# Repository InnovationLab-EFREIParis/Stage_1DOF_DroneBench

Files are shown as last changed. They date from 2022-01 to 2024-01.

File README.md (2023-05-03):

# Bras à un degré de liberté (1DOF Drone Bench)
Dispositif pédagogique permettant de faire découvrir quelques principes et composants que l'on peut retrouver sur un drone mais de façon largement simplifiée et en toute sécurité.  
Le principe est d'asservir un bras mobile (qui par défaut est à la verticale) à un angle voulu en pilotant le moteur et l'hélice fixés à l'extremité de ce bras. La mesure de l'angle se fait par une centrale inertielle. Le tout est controlé par un microcontrôleur relié à un PC où une interface en Python trace différentes courbes (angle en fonction des gazs, angles en fonction du temps).

# Exemple de courbe
L'interface graphique génére une page visible dans un navigateur où l'on peut voir la consigne angulaire et la position du bras évoluant au cours du temps.
Les données brut issues de la centrale sont egalement disponible, ainsi que quelques indications sur les temps de réponses, dépassement...

https://ilab.efrei.fr/html/brasdrone

# Dispositif
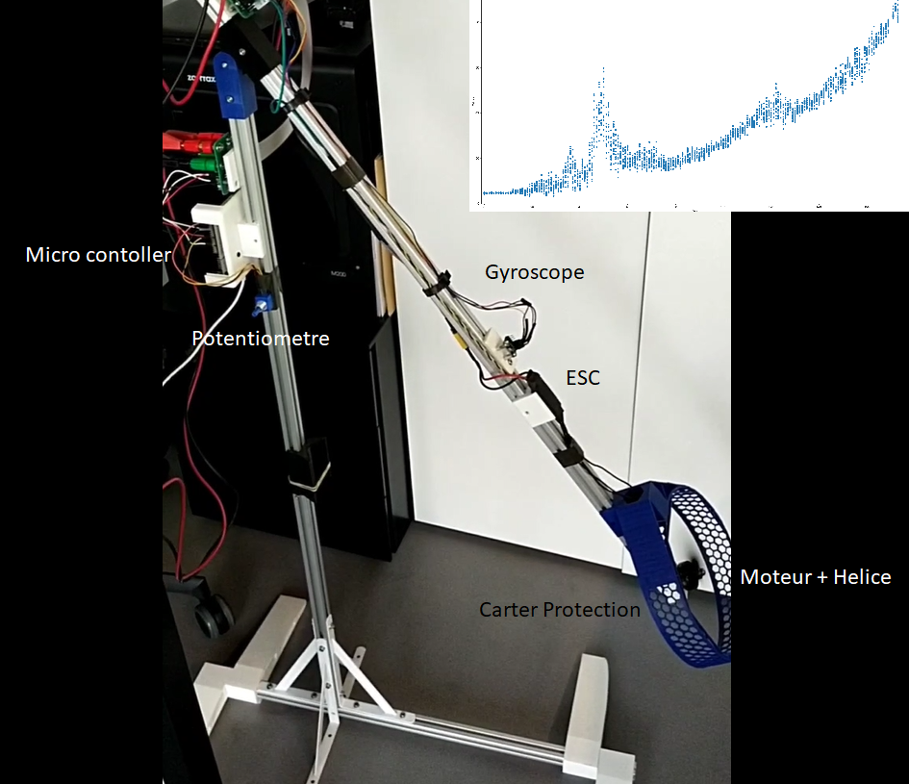
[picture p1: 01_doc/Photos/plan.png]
This is an image


[Vidéo](https://github.com/InnovationLab-EFREIParis/Stage_1DOF_DroneBench/blob/main/01_doc/Photos/video_20220902_181232.mp4)

# Utilisation
## Alimentation
La carte microcontrôleur est alimentée par USB. Il faut donc la connecter à un PC, ce qui permet egalement d'échanger des données.  
La partie moteur est alimentée par les câbles bananes. Régler l'alimentation sur 24V avec une limitation de courant à 5A.  
## Commandes
Ouvrir ensuite un [terminal série](https://github.com/InnovationLab-EFREIParis/Stage_1DOF_DroneBench/tree/main/04_UART_Term/UART_Terminal_1.2.2) puis établir la communication à 115200 bits/s.  
Le microcontrôleur se comporte comme un automate. En envoyant des commandes via la liaison série, il va entrer dans différent états, dont certains seront propres aux différents modes de fonctionnement du dispositif.  
Le mode dans lequel se trouve l'automate s'affiche à l'écran.  
Par défaut, la carte est dans l'état "Entrance" : tapez sur la touche Entrée et suivez les indications à l'écran.  
Une fois l'état "Init UC" passé, la série de "bip" émis par le moteur doit s'arrêter. Le moteur est prêt.  
L'état suivant "Motor Ready" fait office de menu de sélection de mode.  
## Mode automatique
Le mode "Auto Mode" vous permettra de renseigner une consigne de position angulaire, ainsi que des coefficients PID. Il s'agit du seul mode asservis.  
## Modes manuels
Le mode "Manual Mode Pot" vous permettra de modifier manuellement les gazs du moteur via le potentiomètre.  
Le mode "Manual Mode Term" vous permettra de jouer sur une consigne en % de gazs du moteur.  
# Conception
## Mécanique
Une bonne partie des pièces ont été conçues avec Solidworks et fabriquées en impression 3D par dépot de filament.  
Les modèles 3D sont accessibles [ici](https://github.com/InnovationLab-EFREIParis/Stage_1DOF_DroneBench/tree/main/03_mdl)  
Les montants sont en profilé d'aluminium de 20 mm dont voici la [référence](https://github.com/InnovationLab-EFREIParis/Stage_1DOF_DroneBench/tree/main/01_doc/Structure%20et%20assemblage)  
## Électronique
- [Carte microcontrôleur STM32 L476RG](https://github.com/InnovationLab-EFREIParis/Stage_1DOF_DroneBench/tree/main/01_doc/STM32)
- [Moteur et ESC](https://github.com/InnovationLab-EFREIParis/Stage_1DOF_DroneBench/tree/main/01_doc/Moteur%20et%20ESC)
- [Centrale inertielle](https://github.com/InnovationLab-EFREIParis/Stage_1DOF_DroneBench/tree/main/01_doc/Centrale%20inertielle)
# IHM
## Installation
- Bibliothèques à installer : tkinter / serial / pandas / matplotlib     
- Seul le fichier ["Master"](https://github.com/InnovationLab-EFREIParis/Stage_1DOF_DroneBench/blob/a495668b303d1658d739c43df9a72356ac64ced2/06_IHM/Fichiers%20Python/GUI/Master.py) doit être exécuté, mais il est nécessaire d'avoir tous les fichiers du dossier GUI.  
## Utilisation
L'IHM est réalisée en Python via la bibliothèque Tkinter. Une fois le fichier "Master" exécuté, il vous sera alors demandé de sélectionner le port COM et le Baud rate (similaire à l'interaction avec le terminal UART).  
Ensuite, vous aurez alors le choix entre 4 modes : les modes "Manual Mode Term" et "Auto Mode" (accessibles également avec le terminal), ainsi que les modes "Calibration" et "Trip Mode" (séquence de vol).  
Le mode "Calibration" nécessite de sélectionner un [fichier .txt](https://github.com/InnovationLab-EFREIParis/Stage_1DOF_DroneBench/blob/9a31ac3b8853a55df0e124fcb4ea317559d65e36/06_IHM/test%20calibration.txt) comportant les lignes d'instructions suivantes : valeur de % de gazs moteur (tabulation) temps d'attente passé sur cette mesure avant l'accès à la ligne suivante. Il est tout à fait possible de modifier le fichier .txt (seulement, veuillez noter qu'une valeur de gazs au-delà de 17% entraînera le bras dans une position supérieure à 90°, ce qui n'est pas recommandé).  
Le mode "Trip Mode" (ou séquence de vol) nécessite également la sélection d'un [fichier .txt](https://github.com/InnovationLab-EFREIParis/Stage_1DOF_DroneBench/blob/9a31ac3b8853a55df0e124fcb4ea317559d65e36/06_IHM/test%20trip.txt) comportant les lignes d'instructions suivantes : valeur consigne de position angulaire (tabulation) temps d'attente avant la prochaine consigne. Il est également possible de modifier les consignes, cependant veuillez noter qu'il n'est pas possible de renseigner des valeurs d'angles supérieures à 90°.

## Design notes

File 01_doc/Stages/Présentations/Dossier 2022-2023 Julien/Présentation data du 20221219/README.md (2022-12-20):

# Explications relatives au fichier "Données et courbes - comportements statique et dynamique"

## Comportement statique -> feuille "Statique"

Cette feuille comporte des données issues d'un "test calibration" consistant à récupérer les valeurs de positions angulaires,
calculées à partir des données brutes de la centrale inertielle du bras, pendant un certain temps t définis par l'utilisateur (ici 20s).
Les valeurs de consignes sont exprimées en % de gaz du moteur.
La simulation poursuit donc la routine suivante : l'utilisateur choisit une valeur de gaz (%) de départ (ici 1%), 
une valeur finale (dans ce cas-ci 17%), une valeur d'incrémentation (dans cet exemple, tous les 1%) et enfin une valeur de temps d'attente
entre la prise en compte de la valeur consigne et le début de l'enregistrement des valeurs de positions angulaires.

Ce temps d'attente permet donc de prendre uniquement en compte, les valeurs de positions, une fois que le bras s'est stabilisé
(et non pas durant le changement de valeur de gaz).
On va donc avoir par exemple, un envoi de consigne de valeur de gaz de 2%, un délai de 10s durant laquelle on s'assure que le bras
a eu le temps de se stabiliser, et on récupère ensuite les données de positions pendant 20s, avant de prendre en compte la valeur
consigne de gaz suivante (soit 3%).

La valeur de départ est de 1% et non 0%, car la valeur de '0' serait comprise par notre machine d'état comme une demande d'arrêt
des moteurs (le mode atterissage). 
La valeur finale est de 17% car au delà, le bras tend à basculer au dessus de 90° et se bloque.

En 20s d'acquisition, nous arrivons à récupérer autour de 64-65 valeurs de positions pour une valeur consigne (%).
Petite précision concernant la valeur de départ de 1%, le moteur ne s'allume qu'à partir d'une valeur consigne de 2%.
A 1% le moteur est donc encore éteint, mais nous faisons tout de même l'acquisition de valeurs de positions 
(qui sont pour certaines, hors normes, car le bras est considéré en position de départ autour de 0°).

La courbe orange correspond au tracé des valeurs moyennes des valeurs de positions pour chaque valeur consigne.

Commentaires : On constate sur différents essais dont cet exemple, un pic de valeurs de positions élevées pour une valeur consigne de 5%,
ainsi que 2 valeurs consignes (8 et 13 %) dont les valeurs de position ne suivent pas la croissance de la courbe.

## Comportement dynamique -> feuille "Dynamique"

Cette feuille comporte des données issues également d'un "test calibration", mais cette fois-ci nous mesurons la réponse à un échelon,
en prenant en compte, seulement 2 valeurs consignes : 1% (pour les mêmes motivations qu'en statique) puis 10%.
On récupère cette fois-ci les valeurs de position angulaire, sans temps d'attente, durant 15s pour chacune des valeurs.
Ainsi à t=15, on note la transition de la valeur 1% à 10%.

Commentaires : On observe, en cohérence avec le comportement statique, que la courbe oscille jusqu'à se stabiliser autour de la valeur de 30° 
pour 10% de gaz.

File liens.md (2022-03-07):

Les liens postés ici sont ceux des fichiers excel à jour
lien du dossier contenant les fichiers excel
https://drive.google.com/drive/folders/1jXi5AT3fz9ABOeH-yycfwFXTwMAE1G0E?usp=sharing

lien pour la bibliotheque du gyro 
https://github.com/leech001/MPU6050

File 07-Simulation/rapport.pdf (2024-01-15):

# Etude d’un pendulum propuls´e par un moteur RC ´

EFREI Research lab
EFREI - Ecole d’Ing´enieurs G´en´eraliste du Num´erique ´

January 15, 2024

Abstract

L’objectif de cette ´etude est de d´evelopper une commande pour asservir le pendule `a un angle pr´ecis. Dans un premier temps, on ´etablira l’´equation de mouvement du syst`eme. Ensuite, nous ´etudierons la stabilit´e du syst`eme, et enfin, nous proc´ederons `a l’´etude dans le domaine temporel et fr´equentiel du syst`eme.

## 1 Equation de mouvement

On d´esire mod´eliser le syst`eme dynamique `a un degr´e de libert´e suivant :

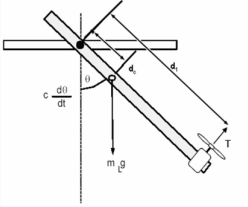
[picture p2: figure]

Figure 1: Pendule propuls´e par un moteur RC

Pour trouver l’equation de mouvement du systeme on utilise la seconde loi de mouvement de Newton :

F = m.a

Ainsi toujours selon la seconde loi de Newton, on a :

τ = I.α

Avec τ le torque en N/m, I le moment d’inertie et α l’acc´el´eration angulaire.
Un pendule avec un bras solide peut ˆetre exprim´e comme la somme des moments d’inertie du bras et du moteur.

Itotal = Ibras + Imoteur

On commence par calculer le moment d’inertie du bras :

Ibras =

Z L

0

x

2 mbras
g

dx

=

mbras.L²
3
Maintenant, on calcule le moment d’inertie du moteur en consid´erant que le moteur est un point de masse `a la fin du bras :

Imoteur =

Z L

0

x

2 mmoteur
g

dx

= mmoteur.L²

Ainsi on a :

Itotal =

1
3

.mbras.L² + mmoteur.L²

L’acc´el´eration angulaire est donn´ee par ¨θ.

Le torque produit par la gravite vaut :

τ = −mgsin(θ)

Le torque produit par la poussee vaut :

τ = T hrust.L

On a donc :

τ = c

˙θ − mgsin(θ) + L.T hrust

I

¨θ = c

˙θ − mgdsin(θ) + L.T hrust

I

¨θ + c

˙θ + mgdsin(θ) = L.T hrust

˙θ(0) = 0; θ(0) = 0

On constate que cette ´equation diff´erentielle du 2`eme ordre est non lin´eaire. Nous devons la lin´eariser pour obtenir la fonction de transfert.
Pour cela, on peut utiliser : l’approximation par petits angles ou on peut trouver le jacobien de l’´equation et la lin´eariser autour d’un point fixe. Commen¸cons par l’approximation des petits angles. Le terme non lin´eaire est sin(θ). On cherche `a approximer cet angle.
D’apr`es la s´erie de Taylor, on a pour sin(θ) :

sin(θ) = θ −

θ

3
3! +

θ

5
5! −

θ

7
7! ...

Les termes apres θ sont tres petits, On en deduit :

sin(θ) ≈ θ

On cherche le jacobien au point fixe (nπ,0) pour tenir compte du point d’equlibre (0,0). :

x1 = θetx2 = ˙θ.

x˙1 = x2

x˙2 =

L
I

.T hrust −

c
I

x2 −

mgd
I

sin(x1)

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
Avec f1 = ˙x1 et f2 = ˙x2
On obtient :

J =

0 | 1
−

mgd
I

cos(nπ) −

| c I

Au point d’equilibre (nπ,0), si n est paire on a 1 et si n est impaire on a -1.
Ainsi, nous nous retrouvons avec un systeme lineaire sous la forme :

x˙ = Ax + Bu

y = Cx + Du

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
I | − c
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
Avec :
A l’etat du systeme,
B la matrice de commande,
C la matrice d’observation, D la matrice d’action directe, x le vecteur d’etat,
u le vecteur de commande,
y le vecteur de sortie.

## 2 Analyse temporel

Afin de contrˆoler le syst`eme, on doit s’assurer qu’il soit stable et contrˆolable.
Pour s’assurer de la stabilit´e, on cherche `a trouver les valeurs propres de la matrice A. Afin de pouvoir continuer dans l’analyse de la stabilite du systeme, on donne des valeurs arbitraires a notre systeme : m = 0.3, g = 9.81, d = 0.5, I = 0.13 et c = 0.1, L = 1.
−λ | 1
−

mgd
I −λ −

c
I

On cherche le d´eterminant :
a b

c d
= ad − bc

On a :
∆ = bλ² + cλ + mgd
I
bλ² + cλ + mgd
I

= 0

λ1 = −c +

p
−4Imgd + c

2
2I

λ2 = −c −

p
−4Imgd + c

2
2I
En remplacant les variables par les valeurs mention´ees plus haut, on a :

λ1 = −0.3846 + 3.3423i

λ2 = −0.3846 − 3.3423i

On constate que les parties r´eels sont n´egatives donc syst`eme est stable.

Figure 2: Portrait de phase

D´esormais, on v´erifie que le syst`eme est controllable. Si la matrice :

ctrb =

A AB

si son rang est ´egal au nombre d’´etats, ici 2. Si oui, dans ce cas on peut choisir n’importe quel valeur propre pour rendre le syst`eme plus stable.

Pour trouver le rang de la matrice ctrb on peut la mettre sous forme ´echelonn´ee r´eduite. On a :

rref =

−11.3 0.77 5.92
0 | 1 | 7.69

Le rang d’une matrice est le nombre de lignes non nulles dans la matrice r´eduite, donc le rang est 2. On en d´eduit que le syst`eme est controllable.

## 3 Analyse fr´equentielle

Pour ´etudier le syst`eme au niveau frequentiel, nous devons obtenir la fonction de transfert du syst`eme. On possede l’equation differentielle du second ordre ainsi que la representation d’etat du systeme. On peut donc trouver la fonction de transfert avec deux methodes :
Methode en partant de la representation d’etat :

H(s) = Y (s)
U(s)

= C(sI − A)

−1B + D

H(s) = | L Js² + cs + mgd

Methode en partant de l’equation de mouvement :

Jθ′′ + cθ′ + mgdθ = thrust · L

On utilise la transformee de Laplace :

Js²Θ(s) + csΘ(s) + mgdΘ(s) = Thrust(s) · L

On isole Θ(s):

(Js² + cs + mgd)Θ(s) = Thrust(s) · L

H(s) = Θ(s) Thrust(s)
=

L
Js² + cs + mgd

Il est important de noter que sur MATLAB, en utilisant la fonction ss2tf(A,B,C,D) on obtient une fonction de transfert avec des valeurs differentes. Cependant son comportement frequentielle est identique. On cherche dans un premier temps la reponse impulsionnelle et la reponse indicielle de la fonction de transfert.
Reponse impulstionelle :
| h(t) = L

−1
{H(s)}
| h(t) = L

−1

Y (s)
X(s)

y(t) = h(t)

reponse indicielle :

s(t) = L

−1

H(s)
s

s(t) = L

−1

Y (s)
X(s) · s

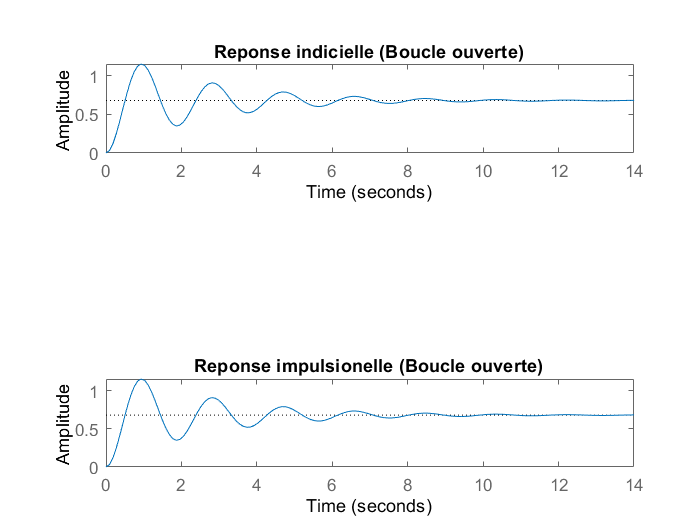
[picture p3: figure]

Figure 3: Reponse indicielle et impulsionnelle

On remarque que le systeme, met environ 5 secondes pour se stabiliser.

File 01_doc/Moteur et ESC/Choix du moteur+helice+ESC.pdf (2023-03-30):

### PROCESSUS DU CHOIX DU MOTEUR+HÉLICE+ESC

Pour le besoin de notre stage nous avions besoin de choisir un moteur et une hélice correspondant à la charge à soulever.
Les caractéristiques à regarder étaient la vitesse de rotation, le couple et l’envergure de l'hélice à choisir.
La vitesse de rotation est synonyme de réactivité, plus le nombre de RPM est élevé plus les mouvements sont rapides mais le couple dans ce cas est faible. Ce paramètre est prédominant dans les constructions axées sur la vitesse et la légèreté.
Par contre les constructions axés sur la stabilité et le déplacement de charges lourdes vont opter pour un couple plus important.
Une autre donnée importante à noter est le nombre de Kv qui se trouve être le voltage multiplié par le nombre de tours minutes, ce paramètre est souvent celui qui est précisé pour connaître la catégorie du moteur que nous choisissons. Plus le nombre de Kv est élevé, plus nous avons de la vitesse, plus il est bas, plus nous avons de couple.
Ce tableau récapitulatif met en lien le nombre de Kv et la taille de l'hélice

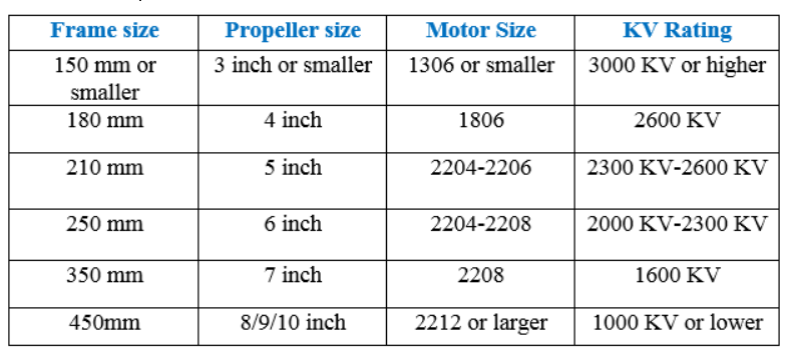
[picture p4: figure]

La charge :
Dans notre cas la charge de manière théorique pouvaient se situer entre 450 grammes et 300 grammes, pour un bras de levier ayant une longueur comprise entre 90cm et 60 cm(500 g/mètre pour le profilé en aluminium). Il faut compter à cela le poids du moteur et celui de l’ESC

Poussée théorique en fonction de la charge :
En théorie on définit la poussée minimale nécessaire qu’un drone doit pouvoir développer en multipliant son poids par deux et ajoutant une marge de 30% de plus du poids du drone, les calculs sont approximatifs et l'équipement pouvant s'avérer plus lourd que prévu.
Cette charge est ensuite répartie sur les 4 moteurs
(Source : Construire son drone)
Pm= Poussée minimale
Nd= Poids du drone
Pu= Poussée moteur unique

Pm = 2.Nd + 30.Nd/100
Pu = Pm/nbre moteurs

Exemple : un drone quadrirotor de 3 kg doit pouvoir développer une poussée minimale de

Pm = 2x3 + 30 x 3/100 = 6+ 0,9 = 6,9 kg de poussée minimale
Pu = 6,9/4 = 1,725 kg

Pour information, cette poussée ne doit pas être atteinte à plein régime mais à un régime avoisinant les 50-60% de la poussée totale dégagée par le moteur. lui permettant de décoller du sol et de se trouver en position stationnaire sans être à plein régime.

Poussée Pratique en fonction de la charge :

Dans notre cas nous devrons prendre en compte le poids du bras du moteur, le poids de l’ESC et aussi le moteur+hélice.
Se retrouvant dans une boucle insolvable nous allons supposer un poids du moteur+hélice de 30 g , 30 g pour l’ESC et un poids de 250 g pour le bras(une longueur de bras de 50cm). Pourquoi une longueur de 50cm? parce que les longueurs supérieures donnaient une poussée minimale située entre 1173 g et 828 g en considérant les mêmes paramètres. Cette puissance devra être développée par un seul moteur à 50-60% de régime: solution faisable mais chère en matériel et gourmande en énergie. Avec un bras plus court nous obtenons une Pm de 703,8g.

Choix du moteur :
Notre choix s’est porté sur le Tmotor T90, qui développe 1300Kv avec les spécifications suivantes :

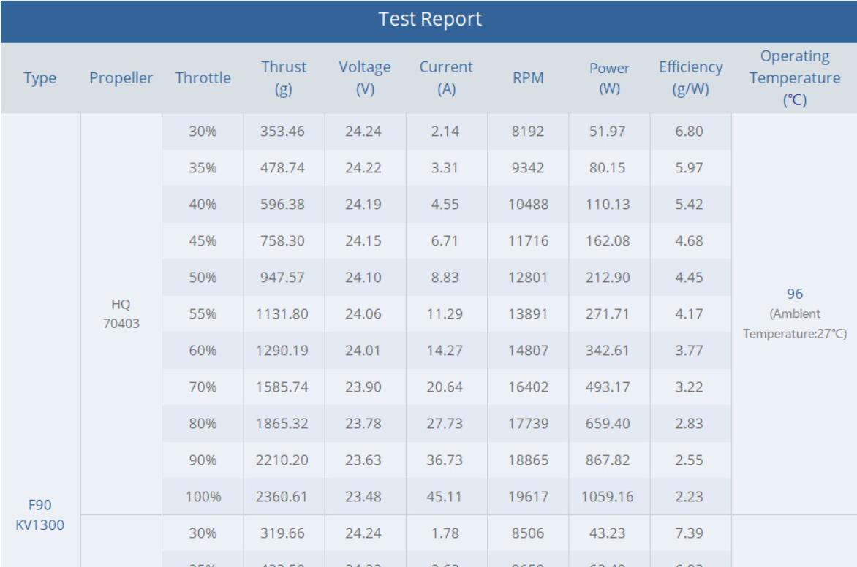
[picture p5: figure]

Nous avons choisi l’ESC avec les spécifications suivantes :

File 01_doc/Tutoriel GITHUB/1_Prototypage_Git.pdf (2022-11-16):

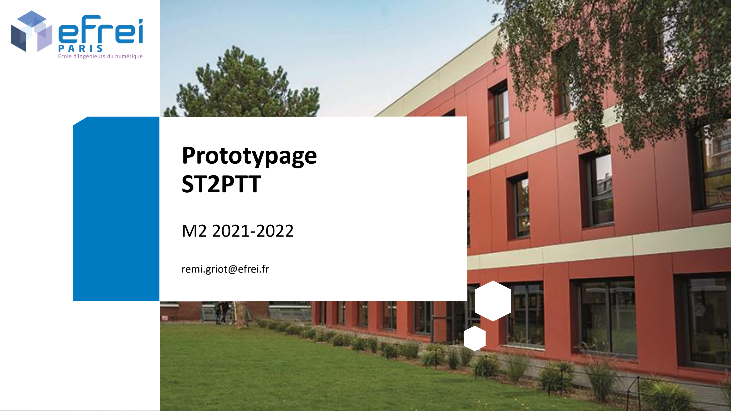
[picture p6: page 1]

remi.griot@efrei.fr

# Prototypage ST2PTT

M2 2021-2022

# 1 Gestion de version avec Git

Rémi Griot
EFREI Paris

# Gestion de version

Intérêt de la gestion de version

Version control systems provide you with three important capabilities: *Reversibility*: the ability to back up to a previous state if you discover that some modification you did was a mistake or a bad idea.
*Concurrency*: the ability to have many people modifying the same collection of files knowing that conflicting modifications can be detected and resolved.
*History*: the ability to attach historical data to your data, such as explanatory comments about the intention behind each change to it. Even for a programmer working solo, change histories are an important aid to memory; for a multi-person project, they are a vitally important form of communication among developers.

# Gestion de version

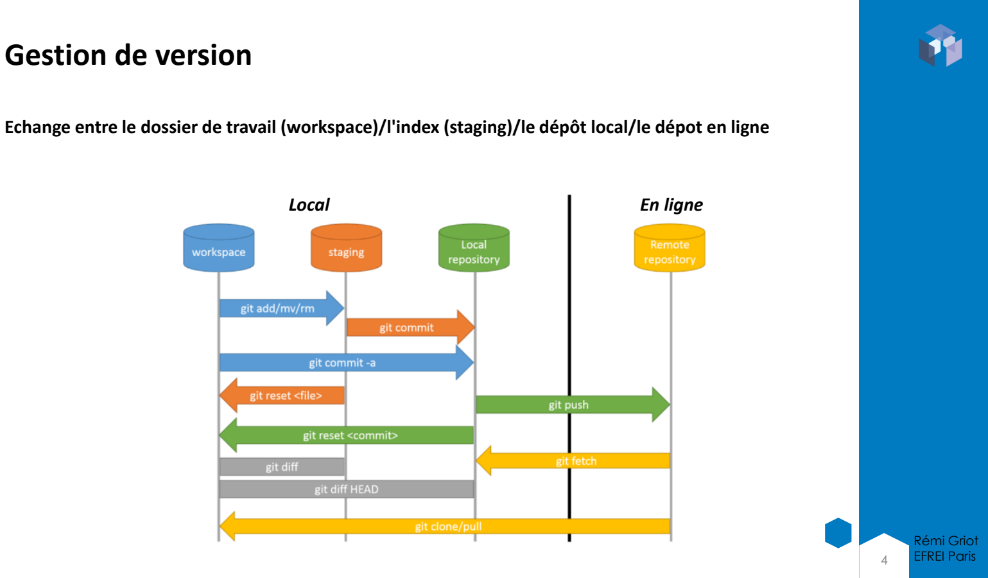
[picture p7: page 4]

Echange entre le dossier de travail (workspace)/l'index (staging)/le dépôt local/le dépot en ligne

Local | En ligne

# Gestion de version

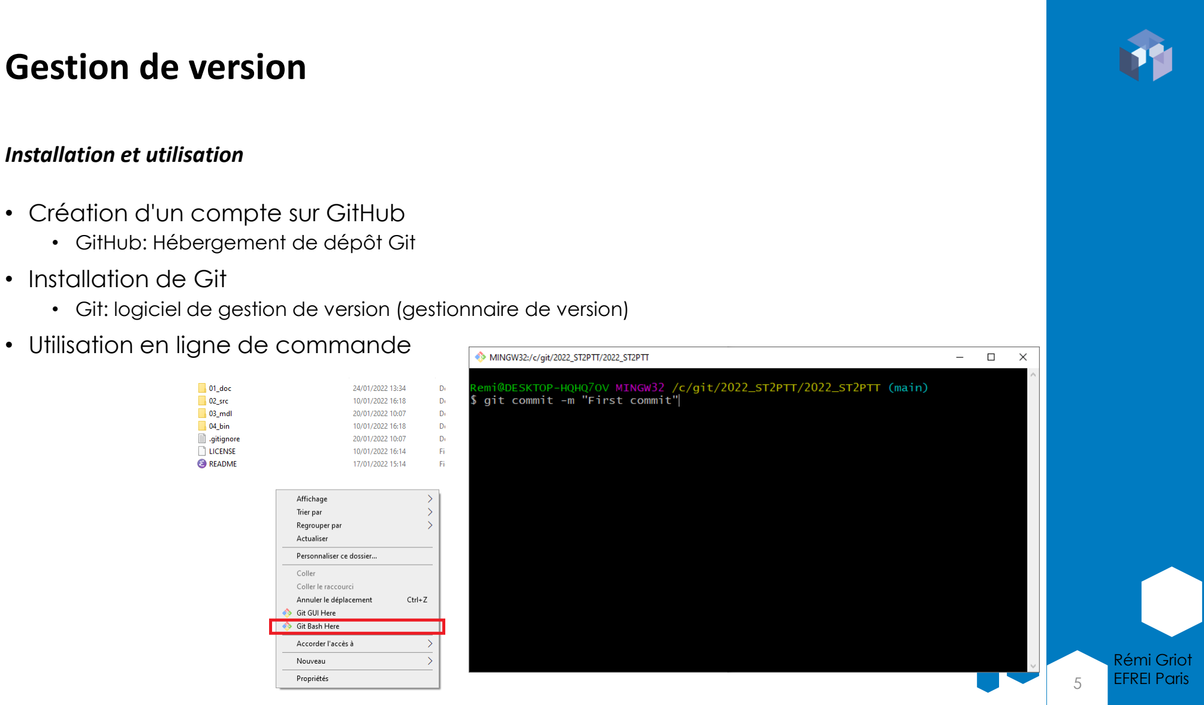
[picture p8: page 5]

- Création d'un compte sur GitHub
- GitHub: Hébergement de dépôt Git
- Installation de Git
- Git: logiciel de gestion de version (gestionnaire de version)
- Utilisation en ligne de commande

Installation et utilisation

# Gestion de version

Configuration

# Clone d'un dépôt (en ligne -> local)

git clone https://github.com/InnovationLab-EFREIParis/Stage_1DOF_DroneBench.git # Initialisation du dépôt (création des fichiers nécessaires à git dans le dossier .git)

git init

Cette commande créait une suite de fichier dans le dossier caché .git
Notamment le fichier .gitignore permettant de lister les fichiers ignorés par le gestionnaire de version

# Gestion de version

Commande agissant en Local

# ajout du fichier monfichier.txt à l'index

git add monfichier.txt

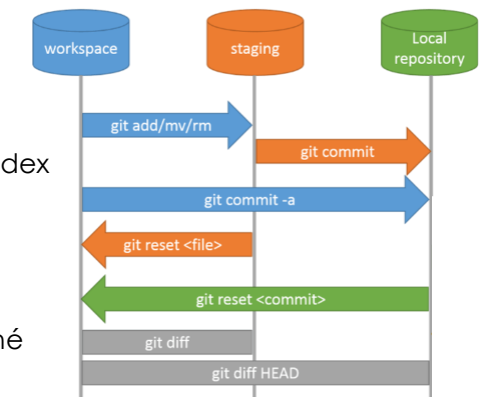
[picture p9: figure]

#ajout de tous les fichiers encore non présents à l'index

git add .
#retire le ficher monfichier.txt de l’index

git rm monfichier.txt
# Sauvegarde en local de ma version, accompagné d’un message "Version 1"

git commit –m "Version 1"
# Statut de la cohérence entre l’index, le dépôt local, et le dossier de travail

git status

# Gestion de version

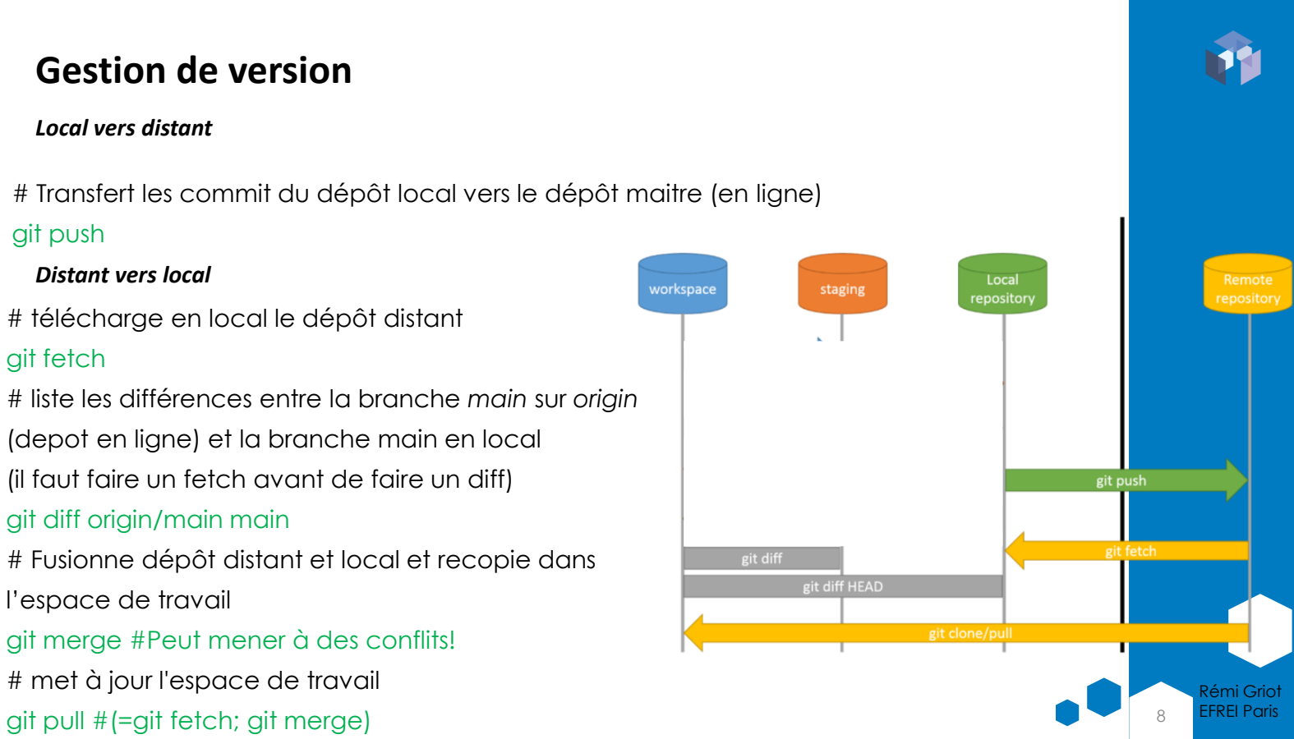
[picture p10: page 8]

Local vers distant

# Transfert les commit du dépôt local vers le dépôt maitre (en ligne) git push

Distant vers local

# télécharge en local le dépôt distant

git fetch
# liste les différences entre la branche main sur origin

(depot en ligne) et la branche main en local
(il faut faire un fetch avant de faire un diff)
git diff origin/main main
# Fusionne dépôt distant et local et recopie dans l’espace de travail

git merge #Peut mener à des conflits!
# met à jour l'espace de travail

git pull #(=git fetch; git merge)

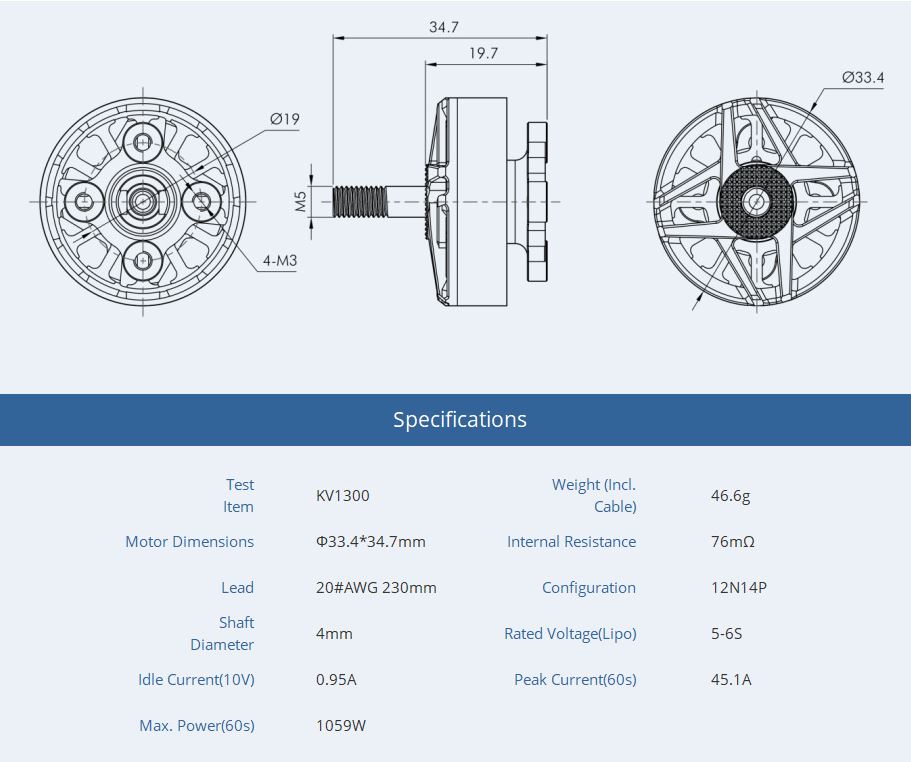
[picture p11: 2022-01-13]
01_doc/Moteur et ESC/spec.JPG

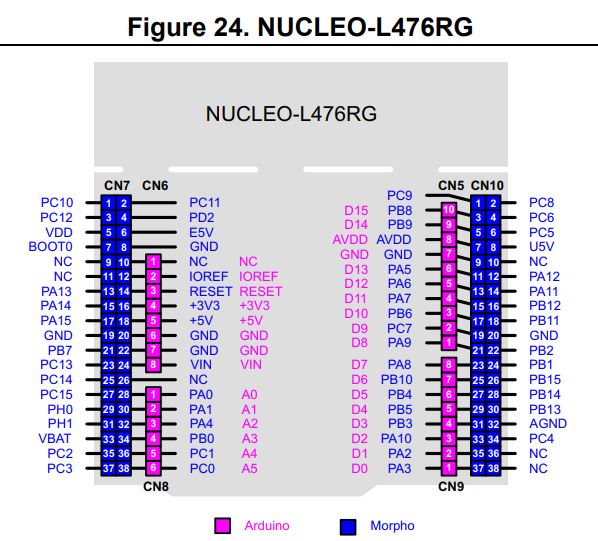
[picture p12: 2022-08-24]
01_doc/STM32/NUCLEO_L476RG_PINOUT.JPG

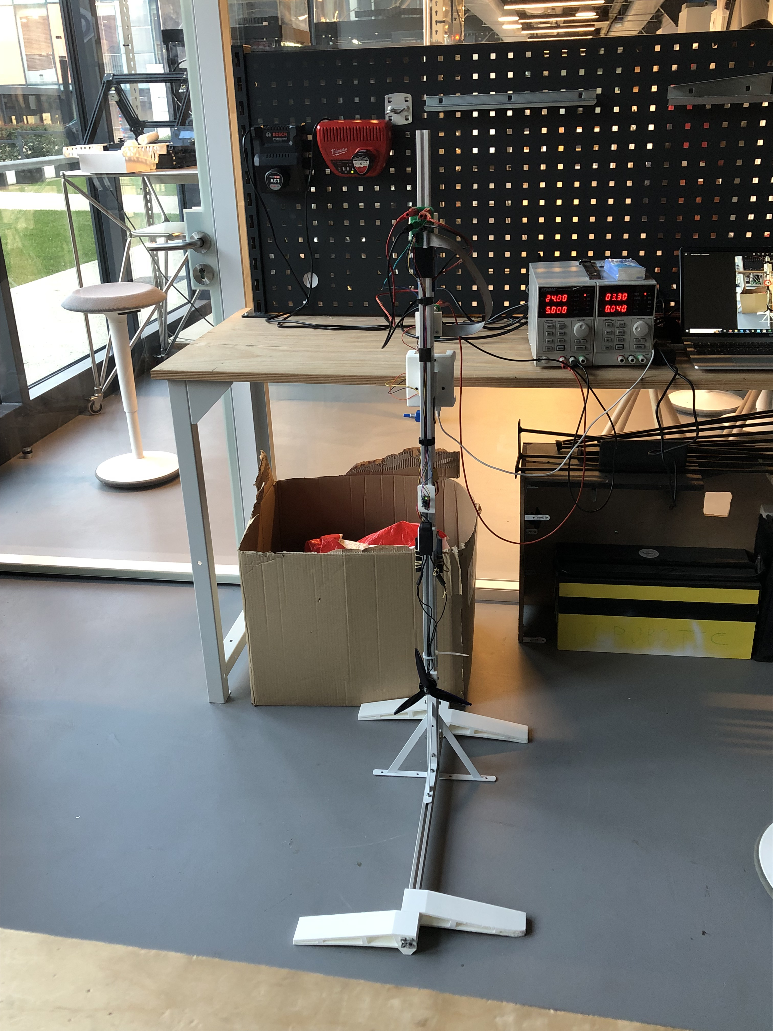
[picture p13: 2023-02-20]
01_doc/Photos/Album 2/Bras vue de face - entier.jpeg

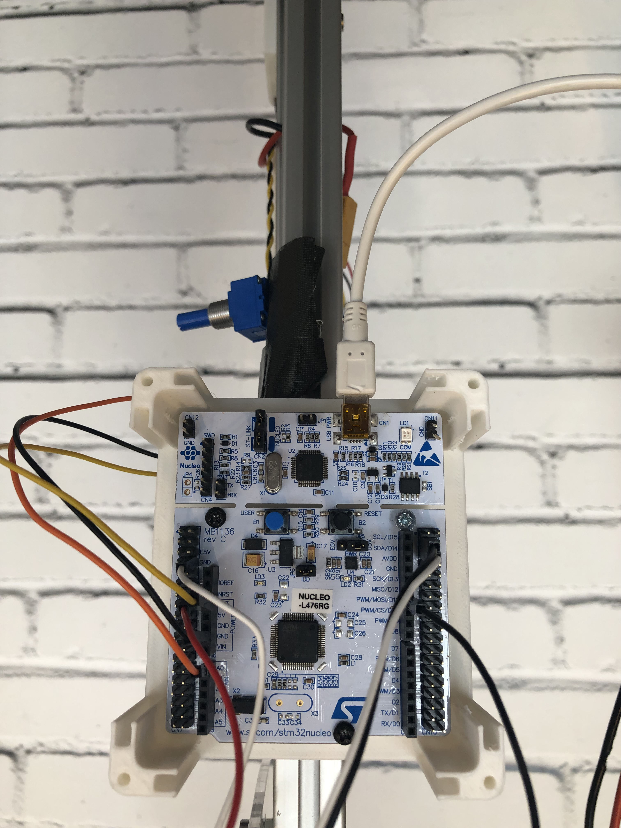
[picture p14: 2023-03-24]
01_doc/Photos/Album 3/STM32.jpg

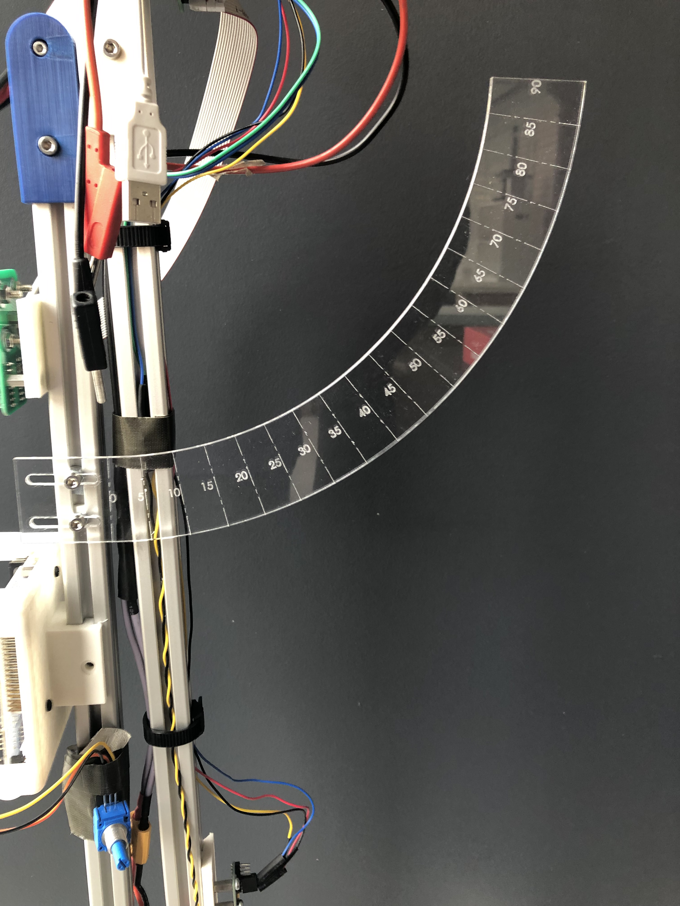
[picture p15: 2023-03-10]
01_doc/Photos/Album 3/Rapporteur.jpg

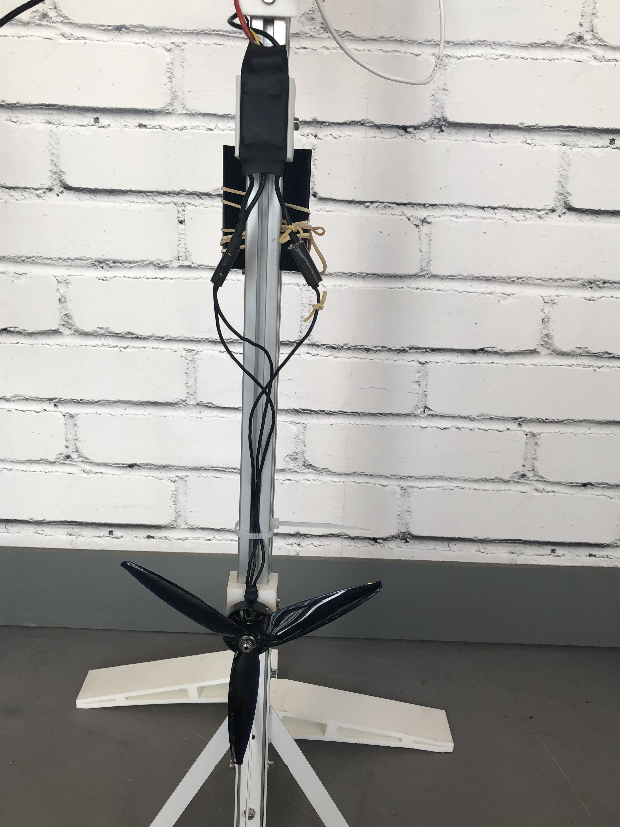
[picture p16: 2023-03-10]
01_doc/Photos/Album 3/Vue de face rapprochée - moteur + esc.jpg

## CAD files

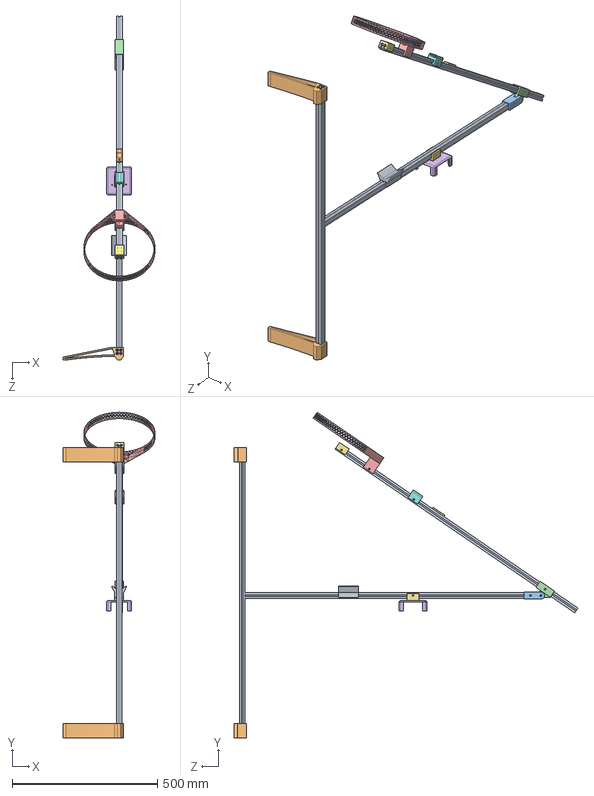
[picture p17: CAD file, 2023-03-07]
03_mdl/sw/assemblage_pied_drone.SLDASM
316.5 x 1121.4 x 1185.0 mm
profil_alu_rs20_efrei x 3
pied_drone_bench x 2
rotule_rs_inf
rotule_rs_sup
Test_carter_helice_rsV5
supportNucleo_rs20
support_moteur_rs4 x 2
Support_esc
shockabsorber
Support MPU

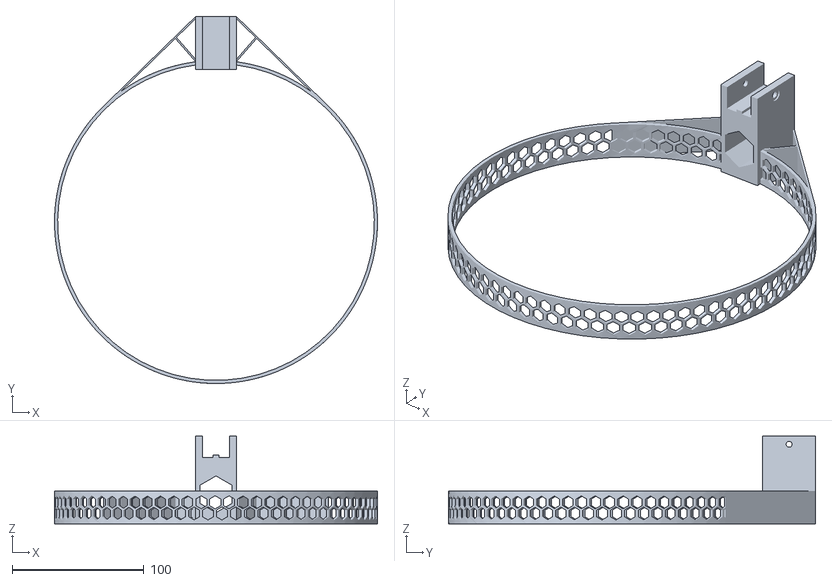
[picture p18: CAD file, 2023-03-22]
03_mdl/stl/Test_carter_helice_rsV5.STL
244.8 x 278.2 x 66.7

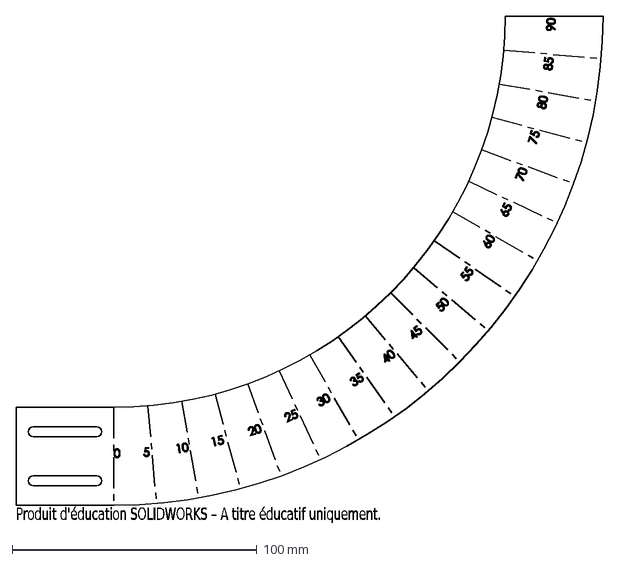
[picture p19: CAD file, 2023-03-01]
03_mdl/sw/Rapporteur 2023/Autres formats/Test rapporteur.DXF
Produit d'éducation SOLIDWORKS – A titre éducatif uniquement.

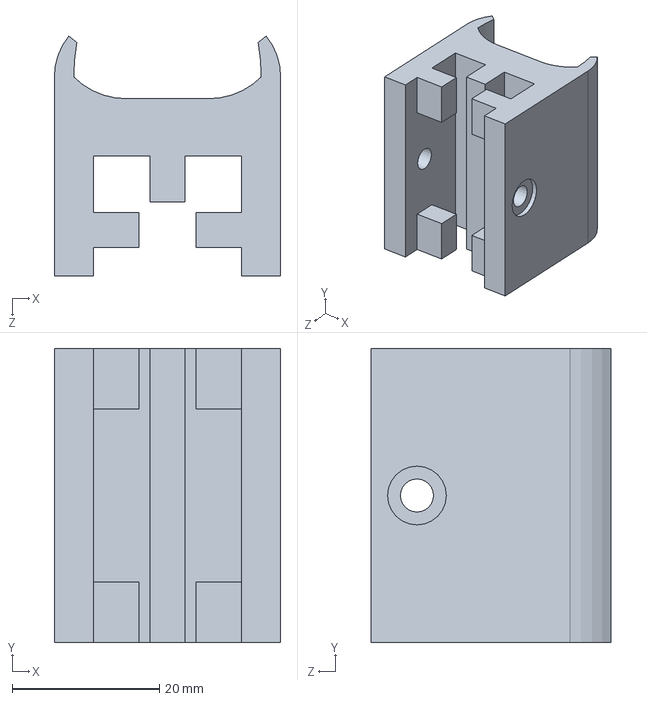
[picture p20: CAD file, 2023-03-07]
03_mdl/sw/Support_esc.SLDPRT
30.8 x 40.0 x 32.6 mm

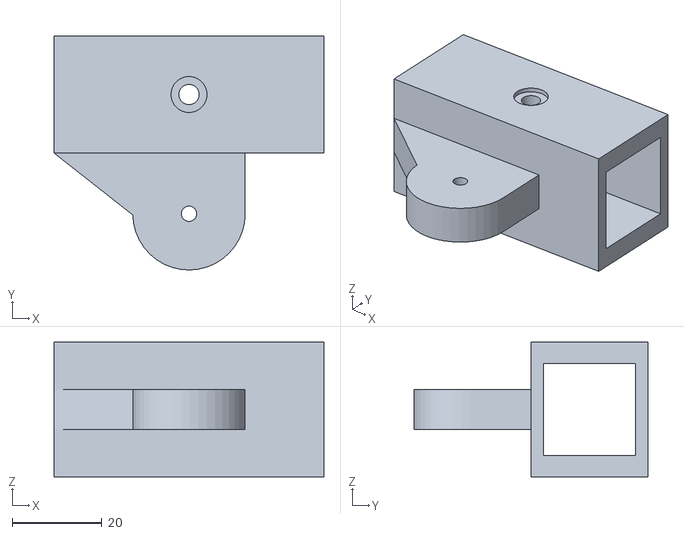
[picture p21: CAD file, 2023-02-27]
03_mdl/stl/rotule_rs_sup.STL
60.0 x 52.0 x 30.0

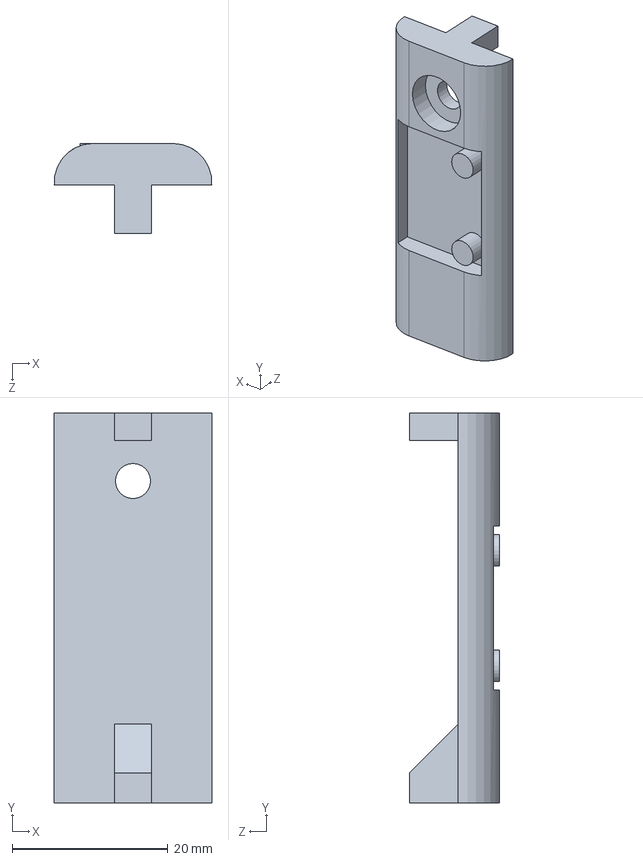
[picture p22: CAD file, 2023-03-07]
03_mdl/sw/Support MPU.SLDPRT
20.2 x 50.0 x 11.6 mm

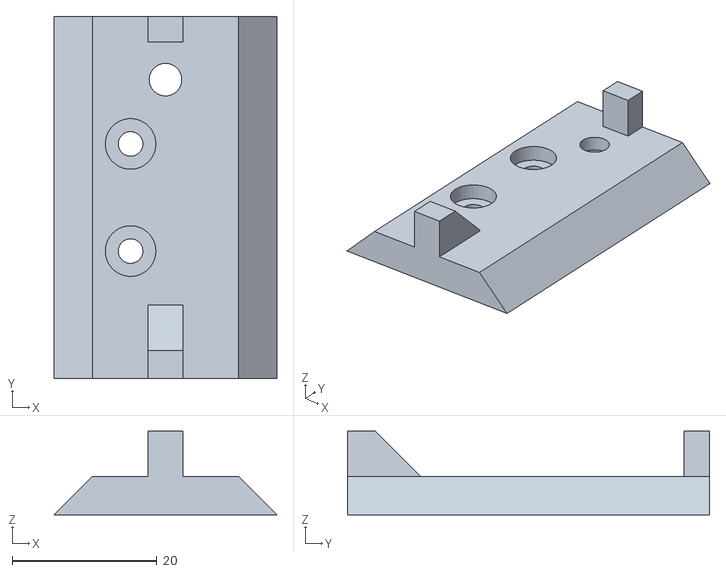
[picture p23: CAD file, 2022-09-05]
03_mdl/stl/Support MPU_rs20.STL
30.8 x 50.0 x 11.6

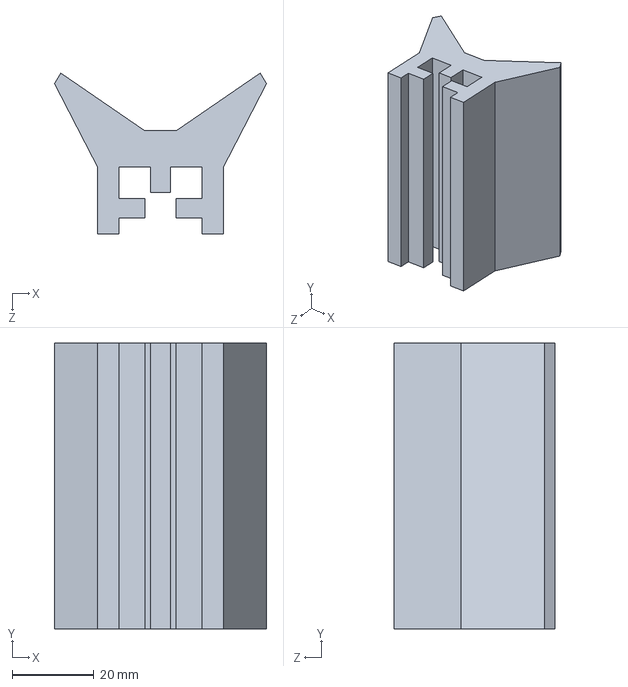
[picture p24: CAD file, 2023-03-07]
03_mdl/sw/shockabsorber.SLDPRT
51.9 x 70.0 x 39.4 mm

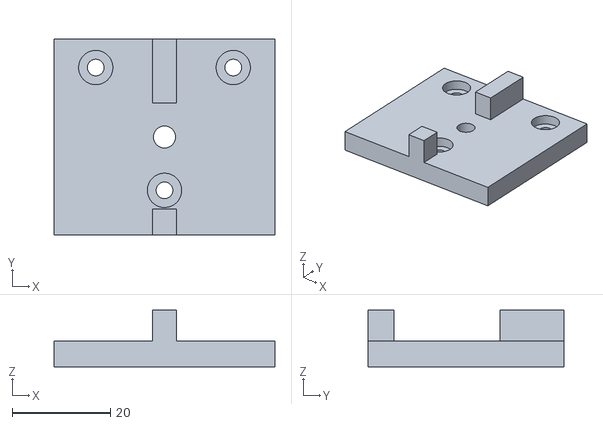
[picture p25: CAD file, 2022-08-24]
03_mdl/stl/Support carte connect.STL
45.0 x 40.0 x 11.6

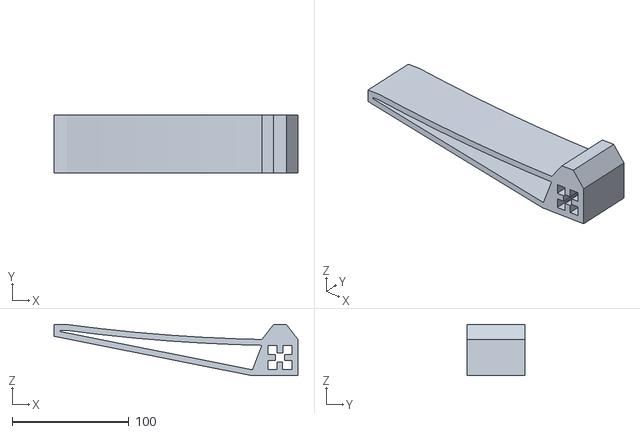
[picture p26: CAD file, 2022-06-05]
03_mdl/stl/pied_drone_bench.STL
208.6 x 50.0 x 43.7

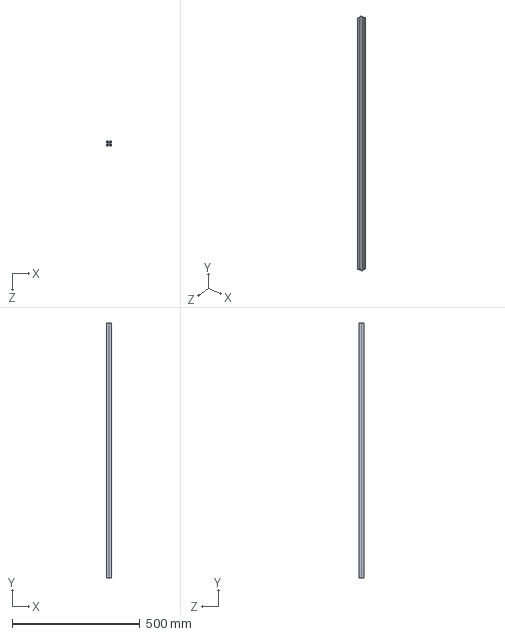
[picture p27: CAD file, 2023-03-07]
03_mdl/sw/profil_alu_rs20_efrei.SLDPRT
20.0 x 1000.0 x 20.0 mm

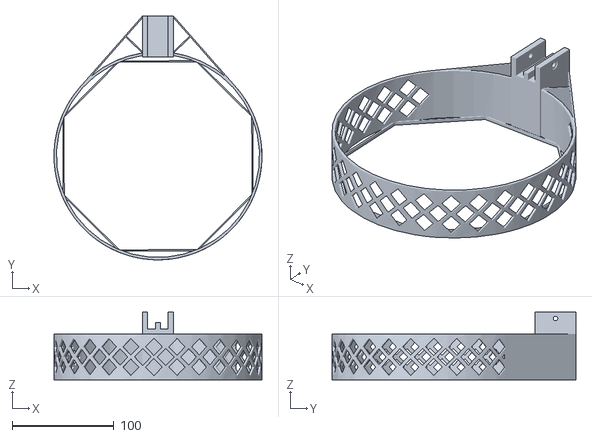
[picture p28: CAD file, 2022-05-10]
03_mdl/stl/carter_helice_rsV4.STL
204.8 x 240.0 x 66.6

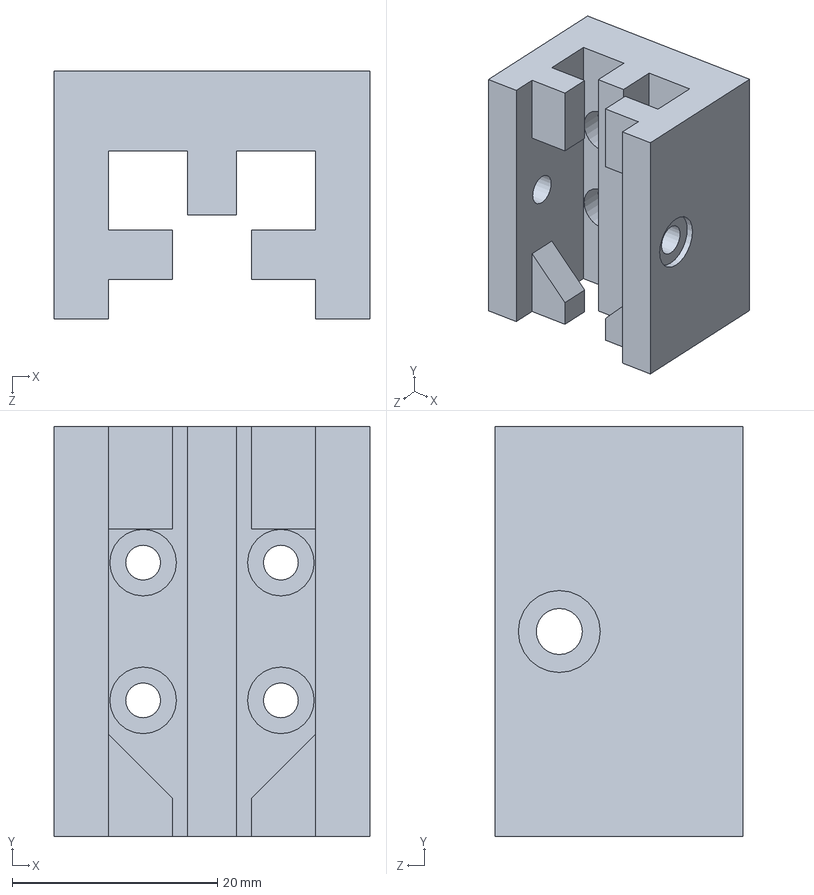
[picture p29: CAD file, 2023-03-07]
03_mdl/sw/support_moteur_rs4.SLDPRT
30.8 x 40.0 x 24.1 mm

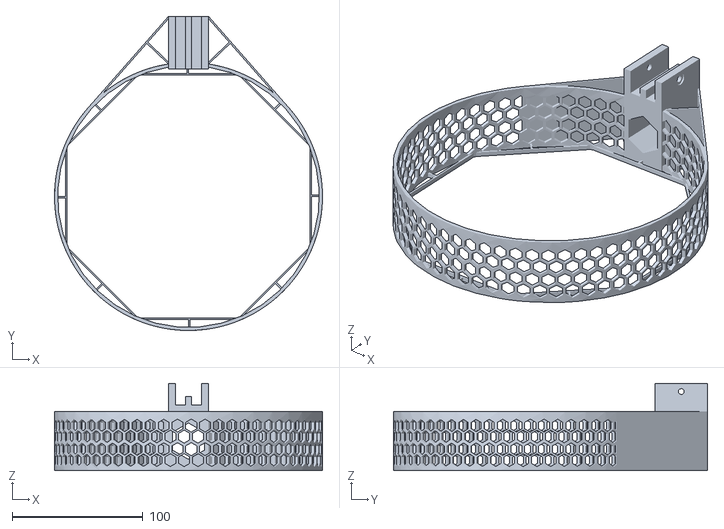
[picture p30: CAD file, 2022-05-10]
03_mdl/stl/carter_helice_rsV5.STL
204.8 x 240.0 x 66.6

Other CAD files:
03_mdl/sw/Rapporteur 2023/Test rapporteur.SLDPRT
03_mdl/sw/supportNucleo_rs20.SLDPRT
03_mdl/stl/support_moteur_rs4.STL
03_mdl/sw/Test_carter_helice_rsV5.SLDPRT
03_mdl/stl/Support MPU.STL
03_mdl/stl/carter_helice_rsV2.STL
03_mdl/stl/nut_rs20.STL
03_mdl/stl/shockabsorber.STL
03_mdl/stl/supportNucleo_rs20.STL
03_mdl/sw/Support MPU_rs20.SLDPRT
03_mdl/sw/Support carte connect.SLDPRT
03_mdl/sw/carter_helice_rsV5.SLDPRT
03_mdl/sw/nut_rs20.SLDPRT
03_mdl/sw/pied_drone_bench.SLDPRT
03_mdl/sw/rapporteur.SLDPRT
03_mdl/sw/rotule_rs_inf.SLDPRT
03_mdl/sw/rotule_rs_sup.SLDPRT

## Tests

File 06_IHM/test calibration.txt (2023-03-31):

Instructions---------------------------------------------------------------------------------------------------------------------------------------------------------------------------------
*This file is an example of the kind of data file you would use with the 'Calibration Mode' from the GUI of the Drone Bench project*
*Please follow the instructions below, if you want to do the simulation correctly*

# First and foremost, we invite you to take into consideration that the data that will be used for the simulation, must be entered this way:

N1	N2

# N1 and N2 are numbers (you must strictly use integers) and they must be separated by a tabulation.
# Be sure not to add any spaces before, between or after the numbers or the line won't be understood as a correct line.
# Do not add any comments on the line, or it will be considered as incorrect.
--------------------------------------------------------------------------------------------------------------------------------------------------------------------------------------------- 

Gas	Time
(‰)	(s)

0	5
10	5

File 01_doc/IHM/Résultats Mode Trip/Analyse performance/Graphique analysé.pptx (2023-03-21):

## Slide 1

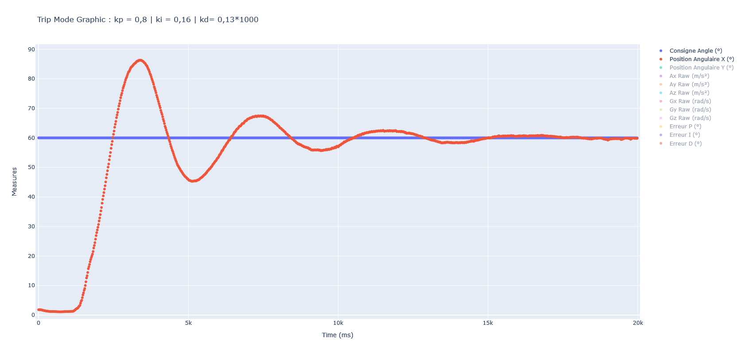
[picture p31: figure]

86,3

D 5% = 43,83%

63

57

54

57,22

6

Tm = 920

Tp = 3420

Tr 5% = 10020

1480

2400

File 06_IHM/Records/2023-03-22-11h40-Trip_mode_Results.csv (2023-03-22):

Consigne Angle (°) | Time (ms) | Position Angulaire X (°) | Position Angulaire Y (°) | Ax Raw (m/s²) | Ay Raw (m/s²) | Az Raw (m/s²) | Gx Raw (rad/s) | Gy Raw (rad/s) | Gz Raw (rad/s) | Erreur P (°) | Erreur I (°) | Erreur D (°)
55 | 0 | 2,79 | -126,64 | 0,3926 | -10,0437 | -0,3319 | 0,0524 | 0,0031 | 0,0072 | 52,21 | 52,21 | 52,21
55 | 20 | 2,86 | -129,29 | 0,395 | -9,9838 | -0,321 | 0,0518 | 0,0041 | 0,0075 | 52,14 | 156,43 | 0,07
55 | 40 | 2,92 | -132,59 | 0,34 | -10,0533 | -0,4979 | 0,0488 | 0,0027 | 0,0047 | 52,08 | 208,52 | -0,06
55 | 60 | 3,02 | -134,45 | 0,3783 | -9,9742 | -0,5387 | 0,0502 | -0,0013 | 0,0077 | 51,98 | 260,5 | -0,1
55 | 80 | 3,03 | -134,46 | 0,3974 | -10,0078 | -0,438 | 0,051 | 0,0033 | 0,0051 | 51,97 | 312,47 | -0,01
55 | 100 | 3,07 | -135,56 | 0,3711 | -9,9503 | -0,5251 | 0,0496 | 0,0027 | 0,0084 | 51,93 | 364,4 | -0,04
55 | 120 | 3,06 | -135,61 | 0,3807 | -9,9982 | -0,438 | 0,0481 | 0,0028 | 0,0079 | 51,94 | 416,34 | 0,01
55 | 140 | 3,06 | -135,81 | 0,3855 | -9,9647 | -0,4625 | 0,05 | 0,0016 | 0,0075 | 51,94 | 468,28 | -0,01
55 | 160 | 3,04 | -135,93 | 0,3615 | -10,0365 | -0,4271 | 0,0506 | 0,0019 | 0,0051 | 51,96 | 520,24 | 0,02
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

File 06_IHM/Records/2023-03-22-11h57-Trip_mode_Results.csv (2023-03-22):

Consigne Angle (°) | Time (ms) | Position Angulaire X (°) | Position Angulaire Y (°) | Ax Raw (m/s²) | Ay Raw (m/s²) | Az Raw (m/s²) | Gx Raw (rad/s) | Gy Raw (rad/s) | Gz Raw (rad/s) | Erreur P (°) | Erreur I (°) | Erreur D (°)
55 | 0 | 2,56 | -139,8 | 0,2873 | -9,9551 | -0,3863 | 0,0496 | 0,004 | 0,0036 | 52,44 | 52,44 | 52,44
55 | 20 | 2,89 | -135,73 | 0,419 | -10,0078 | -0,4625 | 0,0498 | 0,0016 | 0,0064 | 52,11 | 156,86 | -0,2
55 | 40 | 2,96 | -136,16 | 0,3783 | -9,9599 | -0,468 | 0,049 | 0,0025 | 0,006 | 52,04 | 208,9 | -0,07
55 | 60 | 3,04 | -137,23 | 0,3735 | -10,0293 | -0,5305 | 0,0518 | 0,0013 | 0,0076 | 51,96 | 260,86 | -0,08
55 | 80 | 2,96 | -135,43 | 0,3735 | -9,9982 | -0,3183 | 0,0477 | 0,0045 | 0,0033 | 52,04 | 312,9 | 0,08
55 | 100 | 2,98 | -134,13 | 0,4477 | -9,9383 | -0,3836 | 0,0508 | 0,0025 | 0,0087 | 52,02 | 364,92 | -0,03
55 | 120 | 3,0 | -134,36 | 0,3903 | -10,0293 | -0,4598 | 0,0496 | 0,0017 | 0,0075 | 52,0 | 416,92 | -0,02
55 | 140 | 3,01 | -134,95 | 0,3639 | -10,0197 | -0,4788 | 0,0514 | 0,0001 | 0,0064 | 51,99 | 468,91 | -0,01
55 | 160 | 3,0 | -135,44 | 0,3472 | -10,0245 | -0,4571 | 0,0476 | 0,0045 | 0,0072 | 52,0 | 520,92 | 0,01
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

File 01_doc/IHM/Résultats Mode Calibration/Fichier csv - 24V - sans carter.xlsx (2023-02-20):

Gas | PositionX | PositionY | Ax Raw | Ay Raw | Az Raw | Gx Raw | Gy Raw | Gz Raw | Erreur P | Erreur I | Erreur D
0 | 79.49 | -118.35 | 776 | -16680 | -760 | -323 | -18 | 97 | 0 | 0 | 0
0 | 44.23 | -126.53 | 672 | -16696 | -696 | -328 | -14 | 109 | 0 | 0 | 0
0 | 30.96 | -128.95 | 684 | -16668 | -660 | -311 | -8 | 101 | 0 | 0 | 0
0 | 23.81 | -132.8 | 604 | -16656 | -832 | -336 | -25 | 106 | 0 | 0 | 0
0 | 19.12 | -133.63 | 688 | -16632 | -716 | -333 | -12 | 95 | 0 | 0 | 0
0 | 15.59 | -135.69 | 572 | -16672 | -780 | -325 | -1 | 61 | 0 | 0 | 0
0 | 12.78 | -136.68 | 632 | -16660 | -752 | -334 | -18 | 89 | 0 | 0 | 0
0 | 10.4 | -137.75 | 604 | -16632 | -756 | -321 | -10 | 88 | 0 | 0 | 0
0 | 8.39 | -138.12 | 684 | -16572 | -760 | -317 | -5 | 87 | 0 | 0 | 0
0 | 6.65 | -138.13 | 720 | -16604 | -748 | -339 | -10 | 59 | 0 | 0 | 0
0 | 5.11 | -138.84 | 600 | -16664 | -732 | -326 | -6 | 79 | 0 | 0 | 0
0 | 3.82 | -139.08 | 680 | -16764 | -764 | -336 | -10 | 56 | 0 | 0 | 0
0 | 2.78 | -139.47 | 704 | -16648 | -824 | -330 | -6 | 51 | 0 | 0 | 0
0 | 1.89 | -139.34 | 724 | -16744 | -768 | -328 | -39 | 80 | 0 | 0 | 0
0 | 1.17 | -139.15 | 728 | -16696 | -764 | -321 | -11 | 38 | 0 | 0 | 0
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

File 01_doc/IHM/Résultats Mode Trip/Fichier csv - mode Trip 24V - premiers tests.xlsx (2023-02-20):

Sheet: 2023-01-26-13h39-Trip_mode_Resu
kp | ki | kd
0.001 | 0.018 | 0.1
Angle | Temps | PositionX | PositionY | Ax Raw | Ay Raw | Az Raw | Gx Raw | Gy Raw | Gz Raw | Erreur P | Erreur I | Erreur D | Commande | Erreur P : Consigne Angle - Position Angulaire Capteur
60 | 0 | 3.75 | -141.19 | 540 | -16672 | -732 | -305 | -21 | 102 | 56.21 | 1414.93 | 0.06 | 25.53095 | Erreur I : Somme des erreurs P
60 | 20 | 3.38 | -142.3 | 608 | -16732 | -776 | -316 | -56 | 87 | 56.6 | 1471.54 | 0.39 | 26.58332 | Erreur D : Erreur P actuelle - Erreur P précédente
60 | 40 | 3.27 | -142.73 | 612 | -16620 | -732 | -322 | -20 | 75 | 56.69 | 1528.23 | 0.09 | 27.57383
60 | 60 | 3.18 | -143.61 | 572 | -16644 | -904 | -308 | -25 | 80 | 56.79 | 1585.02 | 0.1 | 28.59715
60 | 80 | 3.08 | -142.94 | 660 | -16716 | -656 | -336 | -23 | 75 | 56.93 | 1698.79 | 0.09 | 30.64415
60 | 100 | 2.99 | -143.23 | 568 | -16676 | -816 | -335 | -34 | 80 | 57.01 | 1755.79 | 0.08 | 31.66923
60 | 120 | 2.95 | -143.72 | 608 | -16684 | -872 | -326 | -7 | 90 | 57.04 | 1812.83 | 0.03 | 32.69098
60 | 140 | 2.9 | -144.03 | 620 | -16668 | -864 | -326 | -26 | 80 | 57.08 | 1869.91 | 0.04 | 33.71946
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

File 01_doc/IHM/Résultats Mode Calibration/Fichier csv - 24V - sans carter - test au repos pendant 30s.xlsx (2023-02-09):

Consigne Gaz (‰) | Time (ms) | Position Angulaire X (°) | Position Angulaire Y (°) | Ax Raw (m/s²) | Ay Raw (m/s²) | Az Raw (m/s²) | Gx Raw (rad/s) | Gy Raw (rad/s) | Gz Raw (rad/s)
0 | 0 | 1.27 | -100.13 | 0.2131 | -10.0006 | 0.0136 | 0.0425 | 0.0052 | 0.0123
0 | 20 | 1.37 | -96.2 | 0.2705 | -9.991 | 0.0082 | 0.0462 | -0.0009 | 0.0111
0 | 40 | 1.38 | -96.99 | 0.2442 | -9.9575 | -0.0463 | 0.0433 | -0.002 | 0.0121
0 | 60 | 1.4 | -97.65 | 0.249 | -9.9599 | -0.0517 | 0.0418 | -0.0035 | 0.0131
0 | 80 | 1.39 | -100.06 | 0.2203 | -9.9024 | -0.0979 | 0.0424 | -0.0032 | 0.0117
0 | 100 | 1.39 | -102.38 | 0.2179 | -9.9575 | -0.1143 | 0.0418 | 0.0049 | 0.0112
0 | 120 | 1.43 | -103.77 | 0.2729 | -9.991 | -0.1224 | 0.0452 | -0.0049 | 0.0168
0 | 140 | 1.42 | -102.67 | 0.2298 | -9.9359 | -0.0218 | 0.0434 | -0.0008 | 0.0125
0 | 160 | 1.44 | -102.72 | 0.2586 | -10.0006 | -0.0653 | 0.0442 | -0.0025 | 0.0115
0 | 180 | 1.47 | -102.97 | 0.2849 | -9.9527 | -0.0816 | 0.0418 | -0.0025 | 0.0123
0 | 200 | 1.46 | -105.14 | 0.2107 | -9.991 | -0.1388 | 0.0422 | -0.0028 | 0.0101
0 | 220 | 1.46 | -106.2 | 0.2251 | -9.9551 | -0.1061 | 0.0438 | 0.0015 | 0.0145
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

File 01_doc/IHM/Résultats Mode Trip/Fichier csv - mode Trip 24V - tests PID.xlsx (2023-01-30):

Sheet: 0,001 - 0,018 - 0,1
Angle | Temps | PositionX | PositionY | Ax Raw | Ay Raw | Az Raw | Gx Raw | Gy Raw | Gz Raw | Erreur P | Erreur I | Erreur D
60 | 0 | 3.24 | -150.41 | 472 | -16528 | -812 | -330 | -4 | 82 | 56.76 | 1505.6 | 0
60 | 20 | 3.24 | -149.79 | 472 | -16616 | -732 | -318 | -22 | 103 | 56.74 | 1562.34 | -0.01
60 | 40 | 3.23 | -149.52 | 468 | -16720 | -660 | -312 | -6 | 73 | 56.74 | 1619.09 | 0
60 | 60 | 3.23 | -149.51 | 480 | -16548 | -760 | -310 | -12 | 76 | 56.77 | 1675.85 | 0.02
60 | 80 | 3.25 | -149.72 | 476 | -16548 | -976 | -316 | -43 | 74 | 56.78 | 1789.4 | 0
60 | 100 | 3.24 | -149.55 | 512 | -16592 | -828 | -303 | -16 | 93 | 56.76 | 1846.17 | -0.01
60 | 120 | 3.26 | -149.61 | 440 | -16608 | -924 | -328 | -20 | 78 | 56.76 | 1902.92 | -0.01
60 | 140 | 3.26 | -149.66 | 456 | -16640 | -860 | -306 | -18 | 63 | 56.74 | 1959.66 | -0.02
60 | 160 | 3.25 | -149.05 | 488 | -16584 | -720 | -334 | -38 | 88 | 56.74 | 2073.13 | 0
60 | 180 | 3.27 | -149.26 | 480 | -16648 | -956 | -319 | -30 | 81 | 56.75 | 2129.88 | 0.01
60 | 200 | 3.26 | -149.19 | 456 | -16692 | -716 | -333 | -44 | 80 | 56.73 | 2186.61 | -0.02
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

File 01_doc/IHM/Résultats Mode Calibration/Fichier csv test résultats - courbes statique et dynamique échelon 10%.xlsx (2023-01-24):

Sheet: 2023-01-18-14h52-Calibration_mo
Gas | PositionX | PositionY | Ax Raw | Ay Raw | Az Raw | Gx Raw | Gy Raw | Gz Raw
0 | 24.33 | -56.13 | 600 | -16752 | -752 | -352 | -7 | 109
0 | 18.45 | -80.09 | 680 | -16724 | -836 | -367 | 6 | 114
0 | 15.06 | -90.95 | 692 | -16664 | -560 | -331 | 26 | 97
0 | 12.9 | -100.18 | 580 | -16656 | -716 | -356 | -25 | 95
0 | 11.43 | -106.26 | 676 | -16684 | -756 | -344 | -8 | 98
0 | 10.29 | -111.34 | 576 | -16604 | -732 | -365 | -42 | 90
0 | 9.42 | -115.53 | 600 | -16720 | -804 | -344 | -7 | 98
0 | 8.74 | -119.06 | 644 | -16680 | -884 | -340 | 11 | 100
0 | 8.11 | -121.98 | 548 | -16760 | -740 | -345 | -7 | 111
0 | 7.53 | -124.04 | 540 | -16712 | -616 | -367 | -5 | 92
0 | 7 | -125.93 | 528 | -16652 | -612 | -343 | -7 | 93
0 | 6.57 | -128.31 | 512 | -16700 | -768 | -361 | 7 | 100
0 | 6.18 | -130.04 | 600 | -16744 | -756 | -341 | 1 | 94
0 | 5.8 | -131.61 | 540 | -16692 | -672 | -348 | 38 | 104
0 | 5.45 | -133 | 560 | -16716 | -692 | -341 | -7 | 99
0 | 5.14 | -134.31 | 584 | -16656 | -716 | -334 | 10 | 97
0 | 4.89 | -135.57 | 680 | -16588 | -848 | -345 | -22 | 77
0 | 4.63 | -136.2 | 672 | -16728 | -688 | -337 | 4 | 111
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

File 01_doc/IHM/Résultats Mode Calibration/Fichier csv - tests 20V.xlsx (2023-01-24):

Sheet: 2023-01-23-16h51-Calibration_mo
Gas | PositionX | PositionY | Ax Raw | Ay Raw | Az Raw | Gx Raw | Gy Raw | Gz Raw
0 | 2.79 | -138.93 | 456 | -16688 | -508 | -339 | -8 | 50
0 | 2.82 | -138.59 | 560 | -16584 | -624 | -334 | -32 | 101
0 | 2.76 | -137.83 | 540 | -16732 | -568 | -338 | -21 | 74
0 | 2.8 | -139.16 | 524 | -16680 | -680 | -340 | -16 | 75
0 | 2.84 | -140.79 | 504 | -16624 | -696 | -325 | -37 | 82
0 | 2.87 | -143.52 | 444 | -16652 | -728 | -325 | -37 | 88
0 | 2.75 | -141.93 | 492 | -16600 | -520 | -343 | -15 | 98
0 | 2.77 | -140.9 | 556 | -16528 | -608 | -314 | -27 | 73
0 | 2.82 | -140.72 | 560 | -16700 | -664 | -321 | 1 | 93
0 | 2.8 | -140.35 | 528 | -16644 | -608 | -331 | -30 | 90
0 | 2.93 | -140.94 | 588 | -16696 | -764 | -324 | -13 | 82
0 | 2.96 | -141.73 | 520 | -16696 | -708 | -341 | -19 | 80
0 | 2.86 | -139.52 | 540 | -16548 | -484 | -318 | -8 | 95
0 | 2.84 | -139.58 | 520 | -16684 | -620 | -332 | -15 | 91
0 | 2.85 | -141.15 | 456 | -16652 | -700 | -346 | -11 | 99
0 | 2.92 | -141.81 | 548 | -16644 | -752 | -330 | -25 | 64
0 | 2.91 | -140.66 | 576 | -16592 | -584 | -334 | -30 | 95
0 | 2.89 | -139.82 | 560 | -16560 | -580 | -349 | -34 | 78
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

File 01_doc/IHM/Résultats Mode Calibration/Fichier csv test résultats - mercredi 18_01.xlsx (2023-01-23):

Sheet: 2023-01-18-14h52-Calibration_mo
Gas | PositionX | PositionY | Ax Raw | Ay Raw | Az Raw | Gx Raw | Gy Raw | Gz Raw
0 | 24.33 | -56.13 | 600 | -16752 | -752 | -352 | -7 | 109
0 | 18.45 | -80.09 | 680 | -16724 | -836 | -367 | 6 | 114
0 | 15.06 | -90.95 | 692 | -16664 | -560 | -331 | 26 | 97
0 | 12.9 | -100.18 | 580 | -16656 | -716 | -356 | -25 | 95
0 | 11.43 | -106.26 | 676 | -16684 | -756 | -344 | -8 | 98
0 | 10.29 | -111.34 | 576 | -16604 | -732 | -365 | -42 | 90
0 | 9.42 | -115.53 | 600 | -16720 | -804 | -344 | -7 | 98
0 | 8.74 | -119.06 | 644 | -16680 | -884 | -340 | 11 | 100
0 | 8.11 | -121.98 | 548 | -16760 | -740 | -345 | -7 | 111
0 | 7.53 | -124.04 | 540 | -16712 | -616 | -367 | -5 | 92
0 | 7 | -125.93 | 528 | -16652 | -612 | -343 | -7 | 93
0 | 6.57 | -128.31 | 512 | -16700 | -768 | -361 | 7 | 100
0 | 6.18 | -130.04 | 600 | -16744 | -756 | -341 | 1 | 94
0 | 5.8 | -131.61 | 540 | -16692 | -672 | -348 | 38 | 104
0 | 5.45 | -133 | 560 | -16716 | -692 | -341 | -7 | 99
0 | 5.14 | -134.31 | 584 | -16656 | -716 | -334 | 10 | 97
0 | 4.89 | -135.57 | 680 | -16588 | -848 | -345 | -22 | 77
0 | 4.63 | -136.2 | 672 | -16728 | -688 | -337 | 4 | 111
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

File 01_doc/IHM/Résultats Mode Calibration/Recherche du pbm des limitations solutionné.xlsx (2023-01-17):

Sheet: Feuil1
RowMsg:Data:27.83;-2.60;2140;-15144;6520;-463;-984;-238
RowMsg:Data:27.87;-3.02;2020;-13676;7588;-526;788;530
RowMsg:Data:27.68;-2.47;-1428;-15064;6688;-546;-681;78
RowMsg:Data:27.64;-2.08;-636;-13868;7352;-675;620;284
RowMsg:Data:27.47;-1.98;-332;-15032;6916;-516;-960;35
RowMsg:Data:27.53;-2.67;2884;-13832;7444;-529;816;456
RowMsg:Data:27.38;-1.41;-3536;-15324;6188;-538;-793;-90
RowMsg:Data:27.43;-1.73;1616;-13904;7744;-507;790;464
RowMsg:Data:27.23;-1.24;-1456;-15084;6528;-593;-1048;-67
RowMsg:Data:27.32;-2.19;3524;-13764;7228;-448;459;436
RowMsg:Data:27.12;-1.13;-2860;-15488;6168;-530;-605;-73
RowMsg:Data:27.10;-1.66;2008;-14072;7104;-459;479;477
RowMsg:Data:27.03;-0.09;-4588;-15316;6160;-582;-400;-209
RowMsg:Data:27.05;-0.73;2320;-13988;7196;-418;477;251
RowMsg:Data:26.93;0.13;-2536;-15276;6668;-443;-573;-100
RowMsg:Data:26.88;-0.40;1816;-14392;6848;-332;470;53
RowMsg:Data:26.88;1.45;-5608;-15380;5800;-351;-324;-264
RowMsg:Data:26.97;0.70;2684;-14292;7656;-365;514;-256
RowMsg:Data:26.88;0.99;-1068;-15068;7060;-271;-736;-256
RowMsg:Data:27.01;0.06;3372;-13928;7468;-337;586;195
RowMsg:Data:26.89;1.35;-3616;-15272;5980;-261;-360;-190
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

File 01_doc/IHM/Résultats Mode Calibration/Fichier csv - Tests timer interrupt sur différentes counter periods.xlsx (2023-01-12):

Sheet: Feuil1
CP (en s) | Counter period | NB pts/s | NB pts pour 5s
1 | 10000 | 1 | 5
0.5 | 5000 | 2 | 10
0.4 | 4000 | 2.5 | 12.5
0.3 | 3000 | 3.333333333 | 16.66666667 | NB pts | Counter period | (en s) | (en ms)
0.2 | 2000 | 5 | 25 | 50 | 1000 | 0.1 | 100
0.1 | 1000 | 10 | 50
0.02 | 200 | 50 | 250
0.0001 | 1 | 10000 | 50000

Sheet: 2023-01-05-15h09-Calibration_mo
Gas | Position
0 | 4.39
0 | 4.74
0 | 4.72
0 | 4.48
0 | 4.45
0 | 4.48
0 | 4.4
0 | 4.23
0 | 4.34
0 | 4.67
50 | 31.77
50 | 35.23
50 | 35.3
50 | 37.54
50 | 46.38
50 | 53.86
50 | 61.91
50 | 51.07
50 | 45.37
50 | 31.03
100 | 54.79
100 | 33.3
100 | 22.64
100 | 30.77
100 | 28.7
100 | 24.79
100 | 30.41
100 | 37.22
100 | 31.97
100 | 27.47
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

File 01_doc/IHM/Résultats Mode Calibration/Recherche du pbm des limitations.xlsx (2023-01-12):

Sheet: 2023-01-12-11h32-Calibration_mo
Gas | Colonne1 | PositionX | PositionY | Ax Raw | Ay Raw | Az Raw | Gx Raw | Gy Raw | Gz Raw
100 | 0 | -907.75 | -176.23 | 532 | -18360 | 3656 | 7250 | -1305 | -45
100 | 20 | -572.01 | -103.46 | -1664 | -18364 | 3836 | 7987 | -2277 | 63
100 | 40 | -412.72 | -80.15 | 1348 | -17832 | 4496 | 8550 | -2116 | 259
100 | 60 | -318.61 | -54.41 | -3344 | -17700 | 4092 | 9020 | -1060 | -95
100 | 80 | -255.55 | -51.13 | 3368 | -17688 | 4196 | 9490 | 827 | 211
100 | 100 | -209.07 | -36.41 | -3640 | -17932 | 4396 | 9792 | 269 | 229
100 | 120 | -172.52 | -37.32 | 4484 | -17592 | 4240 | 10167 | -1480 | 120
100 | 140 | -143.34 | -28.55 | -2396 | -17960 | 4700 | 10452 | -1589 | -18
100 | 160 | -118.21 | -29.97 | 4524 | -17508 | 4448 | 10815 | -1808 | 57
100 | 180 | -96.54 | -27.27 | 1260 | -16616 | 5388 | 10889 | 82 | 167
100 | 200 | -77.11 | -24.68 | 976 | -17624 | 4936 | 11022 | -672 | 92
100 | 220 | -59.13 | -20.96 | -112 | -16156 | 5968 | 11038 | -214 | 390
100 | 240 | -42.71 | -14.17 | -3596 | -16668 | 5376 | 11010 | -1252 | 144
100 | 260 | -28.1 | -14.78 | 3504 | -16016 | 5920 | 10907 | -1004 | 153
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

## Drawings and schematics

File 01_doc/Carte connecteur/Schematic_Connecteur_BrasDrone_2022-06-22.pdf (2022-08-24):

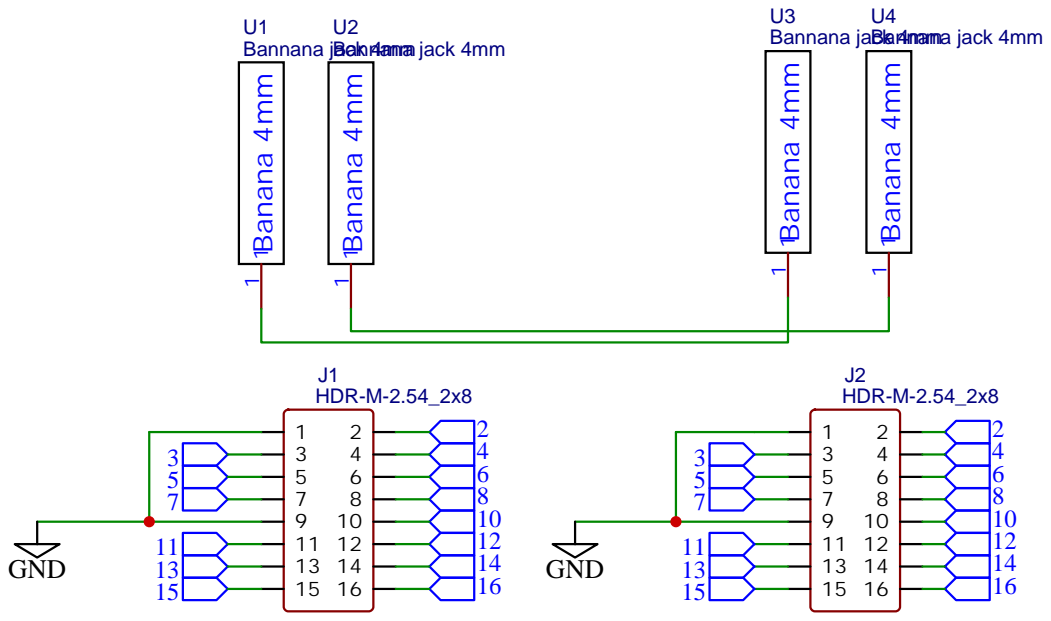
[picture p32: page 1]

Drawn By: remi griot

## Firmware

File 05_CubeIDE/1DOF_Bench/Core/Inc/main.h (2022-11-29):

/* USER CODE BEGIN Header */
/**
  ******************************************************************************
  * @file           : main.h
  * @brief          : Header for main.c file.
  *                   This file contains the common defines of the application.
  ******************************************************************************
  * @attention
  *
  * Copyright (c) 2022 STMicroelectronics.
  * All rights reserved.
  *
  * This software is licensed under terms that can be found in the LICENSE file
  * in the root directory of this software component.
  * If no LICENSE file comes with this software, it is provided AS-IS.
  *
  ******************************************************************************
  */
/* USER CODE END Header */

/* Define to prevent recursive inclusion -------------------------------------*/
#ifndef __MAIN_H
#define __MAIN_H

#ifdef __cplusplus
extern "C" {
#endif

/* Includes ------------------------------------------------------------------*/
#include "stm32l4xx_hal.h"

/* Private includes ----------------------------------------------------------*/
/* USER CODE BEGIN Includes */

/* USER CODE END Includes */

/* Exported types ------------------------------------------------------------*/
/* USER CODE BEGIN ET */

/* USER CODE END ET */

/* Exported constants --------------------------------------------------------*/
/* USER CODE BEGIN EC */

/* USER CODE END EC */

/* Exported macro ------------------------------------------------------------*/
/* USER CODE BEGIN EM */

/* USER CODE END EM */

/* Exported functions prototypes ---------------------------------------------*/
void Error_Handler(void);

/* USER CODE BEGIN EFP */

/* USER CODE END EFP */

/* Private defines -----------------------------------------------------------*/
#define max_period_timer 1999
#define B1_Pin GPIO_PIN_13
#define B1_GPIO_Port GPIOC
#define USART_TX_Pin GPIO_PIN_2
#define USART_TX_GPIO_Port GPIOA
#define USART_RX_Pin GPIO_PIN_3
#define USART_RX_GPIO_Port GPIOA
#define LD2_Pin GPIO_PIN_5
#define LD2_GPIO_Port GPIOA
#define TMS_Pin GPIO_PIN_13
#define TMS_GPIO_Port GPIOA
#define TCK_Pin GPIO_PIN_14
#define TCK_GPIO_Port GPIOA
#define SWO_Pin GPIO_PIN_3
#define SWO_GPIO_Port GPIOB

/* USER CODE BEGIN Private defines */

/* USER CODE END Private defines */

#ifdef __cplusplus
}
#endif

#endif /* __MAIN_H */

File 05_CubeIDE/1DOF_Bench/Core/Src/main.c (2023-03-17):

/* USER CODE BEGIN Header */
/**
 ******************************************************************************
 * @file           : main.c
 * @brief          : Main program body
 ******************************************************************************
 * @attention
 *
 * Copyright (c) 2022 STMicroelectronics.
 * All rights reserved.
 *
 * This software is licensed under terms that can be found in the LICENSE file
 * in the root directory of this software component.
 * If no LICENSE file comes with this software, it is provided AS-IS.
 *
 ******************************************************************************
 */

/*
 * pinout :
 * pot : "3 pins{
 * 	vcc = 3.3v
 * 	signal = A0
 * 	gnd = gnd
 * }
 *
 * ESC : 2 pins{
 *  Signal = D11
 *  gnd = gnd
 * }
 *
 * Gyro : 4 pins{
 * 	vcc = 5v    **brancher sur 3.3
 * 	gnd=gnd
 * 	scl=PB8=d15
 * 	sda = PB9=d14
 *
 *
 * }
 *
 *
 *
 *
 * */

/* USER CODE END Header */
/* Includes ------------------------------------------------------------------*/
#include "main.h"
#include "adc.h"
#include "dma.h"
#include "i2c.h"
#include "tim.h"
#include "usart.h"
#include "gpio.h"

/* Private includes ----------------------------------------------------------*/
/* USER CODE BEGIN Includes */
#include "yann.h"
#include "julien.h"
#include "mpu6050.h"
#include  <stdio.h>
#include  <errno.h>
#include  <sys/unistd.h>
#include  <inttypes.h>
#include  <stdint.h>

/* USER CODE END Includes */

/* Private typedef -----------------------------------------------------------*/
/* USER CODE BEGIN PTD */

/* USER CODE END PTD */

/* Private define ------------------------------------------------------------*/
/* USER CODE BEGIN PD */
/* USER CODE END PD */

/* Private macro -------------------------------------------------------------*/
/* USER CODE BEGIN PM */

/* USER CODE END PM */

/* Private variables ---------------------------------------------------------*/

/* USER CODE BEGIN PV */
Kalman_t kali;
MPU6050_t mpu;

enum states etat, previous_etat;
enum choice_mode choice_mode;

int consigne = 0;
double commande = 0;

int value0 = 0;
int value1 = 0;
int value2 = 0;

int value_prime0 = 0;
int value_prime1 = 0;

int value_kp0 = 0;
int value_kp1 = 0;
int value_kp2 = 0;
int value_kp3 = 0;

int value_ki0 = 0;
int value_ki1 = 0;
int value_ki2 = 0;
int value_ki3 = 0;

int value_kd0 = 0;
int value_kd1 = 0;
int value_kd2 = 0;
int value_kd3 = 0;

// Default coefficients
const int gain_d = 1000;

double kp = 0.001;
double ki = 0.018;
double kd = 0.1;

double erreur = 0;
double _erreur = 0;
double integre_erreur = 0;
double derive_erreur = 0;
char r_buffer[2];
int counter_exceeding_value = 0;

double position_angulaireX = 0;
double position_angulaireY = 0;
double AxRaw = 0;
double AyRaw = 0;
double AzRaw = 0;
double GxRaw = 0;
double GyRaw = 0;
double GzRaw = 0;

const double radtodeg = 57.295779513082320876798154814105;
const double gtoms2 = 9.80665;

char data;

/* USER CODE END PV */

/* Private function prototypes -----------------------------------------------*/
void SystemClock_Config(void);
/* USER CODE BEGIN PFP */

/* USER CODE END PFP */

/* Private user code ---------------------------------------------------------*/
/* USER CODE BEGIN 0 */

uint8_t gaz_buffer[4];

int _write(int file, char *data, int len) {
	if ((file != STDOUT_FILENO) && (file != STDERR_FILENO)) {
		errno = EBADF;
		return -1;
	}

	// arbitrary timeout 1000
	HAL_StatusTypeDef status = HAL_UART_Transmit(&huart2, (uint8_t*) data, len,
			1000);

	// return # of bytes written - as best we can tell
	return (status == HAL_OK ? len : 0);
}

/* USER CODE END 0 */

/**
  * @brief  The application entry point.
  * @retval int
  */
int main(void)
{
  /* USER CODE BEGIN 1 */

	//uint16_t timer_val;
	//uint32_t timer_val2=UINT32_C(1234567890);

	etat = entrance;
	int okay;
	int valeur_can;
	int mapped_value = valeur_min_moteur;

	commande = valeur_min_moteur;
	double landing_value = valeur_min_moteur;
	int timeout_gyro = 1000;

	// mode 2
	int cpt_char = 0;
	int max_cpt_char = 4;
	char r_buffer_string[max_cpt_char];
	int gaz_term_percent = 0;
	// mode 3
	int cpt_char_prime = 0;
	int max_cpt_char_prime = 3;
	char r_buffer_string_prime[max_cpt_char_prime];
	int angle_term = 0;


	int cpt_char_kp = 0;
	int max_cpt_char_kp = 5; //7 avec virgule et chiffre des unités
	char r_buffer_string_kp[max_cpt_char_kp];

	int cpt_char_ki = 0;
	int max_cpt_char_ki = 5; //7 avec virgule et chiffre des unités
	char r_buffer_string_ki[max_cpt_char_ki];

	int cpt_char_kd = 0;
	int max_cpt_char_kd = 5; //7 avec virgule et chiffre des unités
	char r_buffer_string_kd[max_cpt_char_kd];

	char msg_motor_ready[] = "> Press [ SPACE ] for Motor ready\n\r";
	char msg_info_mode[] = "> Press [ ? ] for Info mode\n\n\r";
	char msg_error_char_nb[] =
			"ERROR: Please enter only characters included in this list : 0 1 2 3 4 5 6 7 8 9\n\n\r";
	char msg_error_value_sup[] = "ERROR: Value > 173\n\n\r";
	char msg_error_value_sup_angle[] = "ERROR: Value > 90\n\n\r";

  /* USER CODE END 1 */

  /* MCU Configuration--------------------------------------------------------*/

  /* Reset of all peripherals, Initializes the Flash interface and the Systick. */
  HAL_Init();

  /* USER CODE BEGIN Init */

  /* USER CODE END Init */

  /* Configure the system clock */
  SystemClock_Config();

  /* USER CODE BEGIN SysInit */

  /* USER CODE END SysInit */

  /* Initialize all configured peripherals */
  MX_GPIO_Init();
  MX_DMA_Init();
  MX_ADC1_Init();
  MX_USART2_UART_Init();
  MX_TIM3_Init();
  MX_I2C1_Init();
  MX_TIM2_Init();
  MX_TIM15_Init();
  MX_TIM17_Init();
  MX_TIM16_Init();
  /* USER CODE BEGIN 2 */
	HAL_TIM_PWM_Start(&htim3, TIM_CHANNEL_2);

	// counters to test stuff 15-> 10^-6s / 2-> 10^-7s
	//HAL_TIM_Base_Start(&htim15);
	HAL_TIM_Base_Start(&htim2);
  /* USER CODE END 2 */

  /* Infinite loop */
  /* USER CODE BEGIN WHILE */
	while (1) {

		__HAL_UART_CLEAR_OREFLAG(&huart2);

		// Re-initialization of buffer
		r_buffer[0] = 0;

		//---------changing states-------

		switch (etat) {

			// TAG_UC_001
			// First step: Press ENTER to start the experiment
		case entrance:

			do {
				HAL_UART_Receive(&huart2, (uint8_t*) r_buffer, 1, 10);
			} while (r_buffer[0] != '\r');

			etat = init_uc;

			break;

			// TAG_UC_002
			// State init: initialization of micro-controller
		case init_uc:

			printf("State: Init uc\n\r");

			// -------------------------------------------------------------------------
			// -> démarrer le compteur

			//HAL_Delay(1000);
			//timer_val = __HAL_TIM_GET_COUNTER(&htim15);
			//HAL_Delay(6);
			//timer_val = __HAL_TIM_GET_COUNTER(&htim15) - timer_val ;
			//printf("Time consumed : %d *10^-6 secondes\r\n", timer_val);

			//HAL_Delay(1000);
			//timer_val2 = __HAL_TIM_GET_COUNTER(&htim2);
			//HAL_Delay(10);
			//timer_val2 = __HAL_TIM_GET_COUNTER(&htim2) - timer_val2 ;
			//HAL_TIM_Base_Stop(&htim2);
			//printf("Time consumed : %" PRIu32 " *10^-7 secondes\r\n", timer_val2);
			// -------------------------------------------------------------------------

			printf(msg_motor_ready);
			printf(msg_info_mode);

			printf("\n\r");
			do {
				if (HAL_UART_Receive(&huart2, (uint8_t*) r_buffer, 1, 10)
						== HAL_OK) {
					HAL_UART_Transmit(&huart2, (uint8_t*) r_buffer, 1, 10);
				} else {
					__HAL_UART_CLEAR_OREFLAG(&huart2);
				}
			} while ((r_buffer[0] != ' ') && (r_buffer[0] != '?'));
			printf("\n\n\r");

			switch (r_buffer[0]) {
			case ' ':
				etat = motor_ready;
				break;
			case '?':
				etat = info_mode;
				previous_etat = init_uc;
				break;
			default:
				break;
			}

			break;

			// TAG_UC_003
			// State '?': board of informations
		case info_mode:

			printf("State: Info mode\n\n\r");

			printf("Firmware version %.2f \n\r", firmware_version);
			printf("Baud rate %lu \n\n\r", huart2.Init.BaudRate);

			printf("Angle (auto mode) = %d deg\n\n\r", angle_term);
			printf("kp = %.4f\n\r", kp);
			printf("ki = %.4f\n\r", ki);
			printf("kd = %.4f\n\n\r", kd);

			printf("List of States:\n\r");
			printf(">>Init UC\n\r");
			printf(">>Info Mode\n\r");
			printf(">>Motor Ready\n\r");
			printf(">>Manual Mode Pot\n\r");
			printf(">>Manual Mode Term\n\r");
			printf(">>Auto Mode\n\n\r");

			//go to previous state
			etat = previous_etat;
			break;

			// TAG_UC_005
			// State ' ': motor is ready
		case motor_ready:

			printf("State: Motor ready\n\n\r");

			printf(msg_info_mode);
			printf("> Press [ 1 ] for Manual mode pot\n\r");
			printf("> Press [ 2 ] for Manual mode term\n\r");
			printf("> Press [ 3 ] for Auto mode\n\r");
			printf("> Press [ 4 ] for Trip mode\n\r");

			// Init Motor
			load_pwm(htim3, valeur_min_moteur);
			HAL_Delay(100);

			printf("\n\r");
			do {
				if (HAL_UART_Receive(&huart2, (uint8_t*) r_buffer, 1, 10)
						== HAL_OK) {
					HAL_UART_Transmit(&huart2, (uint8_t*) r_buffer, 1, 10);
				} else {
					__HAL_UART_CLEAR_OREFLAG(&huart2);
				}
			} while ((r_buffer[0] != '?') && (r_buffer[0] != '1')
					&& (r_buffer[0] != '2') && (r_buffer[0] != '3')
					&& (r_buffer[0] != '4'));
			printf("\n\n\r");

			switch (r_buffer[0]) {
			case '?':
				etat = info_mode;
				previous_etat = motor_ready;
				break;
			case '1':
				etat = manual_mode_pot;
				break;
			case '2':
				etat = manual_mode_term;
				break;
			case '3':
				choice_mode = choice_auto;
				etat = init_gyro;
				break;
			case '4':
				choice_mode = choice_trip;
				etat = init_gyro;
				break;
			default:
				break;
			}

			break;

			// TAG_UC_006
			// State '1': manual mode pot
		case manual_mode_pot:

			printf("State: Manual mode pot \n\n\r");

			// Start Init Pot--------------------
			printf("Init pot\n\r");

			HAL_ADC_Start(&hadc1);
			okay = 1;
			printf("> Put the potentiometer at zero\n\r");
			HAL_Delay(100);

			while (okay == 1) {
				HAL_ADC_Start(&hadc1);
				if (HAL_ADC_PollForConversion(&hadc1, 100) == HAL_OK) {
					valeur_can = HAL_ADC_GetValue(&hadc1);
					printf("ADC value : %d \n\r", valeur_can);
				} else {
					printf("Conversion NOK\n\r");
				}
				if (valeur_can <= 20) {
					okay = 0;
				}
				HAL_Delay(1000);
			}

			printf("Success \n\n\r");
			// End Init Pot----------------------

			printf(msg_info_mode);
			printf(msg_motor_ready);

			//recuperation de la pwm
			printf("\n\r");
			do {
				if (HAL_UART_Receive(&huart2, (uint8_t*) r_buffer, 1, 10)
						== HAL_OK) {
					HAL_UART_Transmit(&huart2, (uint8_t*) r_buffer, 1, 10);
				} else {
					__HAL_UART_CLEAR_OREFLAG(&huart2);
				}
				valeur_can = load_adc(hadc1, 5);
				mapped_value = mapping_adc_value(valeur_can);
				HAL_Delay(100);
				load_pwm(htim3, mapped_value);

			} while ((r_buffer[0] != ' ') && (r_buffer[0] != '?'));
			printf("\n\n\r");

			switch (r_buffer[0]) {
			case '?':
				etat = info_mode;
				previous_etat = manual_mode_pot;
				break;
			case ' ':
				landing_value = mapped_value;
				etat = landing;
				break;
			default:
				break;
			}

			break;

			// TAG_UC_007
			// State '2': manual mode term
		case manual_mode_term:

			printf("State: Manual mode term\n\n\r");

			// for now let's say 10 as value max -> 15% = dangerous
			// edit: it can now go up to 10% but only by incrementing by 1% with '+'
			// edit2: I need to increase it to 17% for the GUI
			// edit3: with permil I need to increase it to 173 (/1000) which is equivalent to 17.3%
			printf(
					"> Enter value between 1 and 173 (power percentage) then press [ ENTER ]\n\r");
			printf("> Press [ + ] or [ - ]\n\n\r");
			printf(msg_info_mode);
			printf(msg_motor_ready);
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

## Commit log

2022-01-03 Add solidworks part
    [profil_alu_rs20_efrei.SLDPRT, rotule_rs_inf.SLDPRT, rotule_rs_sup.SLDPRT]
2022-01-04 Add files via upload
    Exercies realisés le 04 Janvier 2022 pour la prise en main de solidWorks
    [Bride.SLDPRT, Etude de cas 1.SLDPRT, Etude de cas 2.SLDPRT, Exercice 1.SLDPRT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]
2022-01-13 add doc about f90 motor
    [support_moteur.SLDPRT]
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2022-02-23 Add files via upload
    support esc
    [Support_esc.SLDPRT]
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2022-03-03 add doc and carter propeller
    [carter_helice_rs.SLDPRT]
2022-03-04 v2 carter
    [carter_helice_rs.SLDPRT, carter_helice_rsV2.SLDPRT, moeteur+protec.SLDPRT, support_moteur_rs4.SLDPRT]
2022-03-07 support gyro
    [Support MPU.SLDPRT, Support MPU.STL, moeteur+protec.SLDPRT]
2022-03-14 clean code with interrupts activated
    [carter_helice_rsV2.SLDPRT, carter_helice_rsV2.STL]
2022-04-01 last pushv2
    [Bride.SLDPRT, Etude de cas 1.SLDPRT, Etude de cas 2.SLDPRT, Exercice 1.SLDPRT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]
2022-04-01 last pushv3
    [moeteur+protec.SLDPRT, supportNucleoTemp.SLDPRT]
2022-04-12 Add supportNucleo_rs20
    [supportNucleo_rs20.SLDPRT]
2022-04-12 Modify Support moteur (conges)
    [support_moteur_rs4.SLDPRT]
2022-04-13 add stl
    [supportNucleo_rs20.STL, support_moteur_rs4.STL]
2022-04-13 Pied de stabilisation
    [pied_drone_bench.SLDPRT]
2022-04-26 add carter v4
    [carter_helice_rsV3.SLDPRT, carter_helice_rsV4.SLDPRT]
2022-05-10 commit carter
    [carter_helice_rsV4.STL, carter_helice_rsV5.SLDPRT, carter_helice_rsV5.STL]
2022-08-24 add support carte connect
    [Support carte connect.SLDPRT, Support carte connect.STL]
2022-08-24 rm model carter
    [carter_helice_rs.SLDPRT, carter_helice_rsV2.SLDPRT, carter_helice_rsV3.SLDPRT, carter_helice_rsV4.SLDPRT]
2022-08-25 nut rs20
    [Support carte connect.SLDPRT, nut_rs20.SLDPRT, nut_rs20.STL]
2022-09-02 rm support nuclo temp
    [supportNucleoTemp.SLDPRT]
2022-09-02 new gyro support and firmware
    [Support MPU_rs20.SLDPRT, Support MPU_rs20.STL]
2022-11-14 add rapporteur
    [rapporteur.SLDPRT]
2022-11-28 compteur et autres
    [Comparaison des temps d'exécutions au sein de la boucle de auto mode.xlsx]
2022-11-29 compteur et julien.c
    [Comparaison des temps d'exécutions au sein de la boucle de auto mode.xlsx]
2022-12-15 dev IHM - calibration et séquence de vol
    [Fichier csv test résultats - boîte à moustaches.xlsx]
2022-12-19 dev IHM - tests calibration
    [Fichier csv test résultats - boîte à moustaches.xlsx, Fichier csv test résultats - nuage de points.xlsx]
2022-12-20 dossier data + readme
    [Comparaison des temps d'exécutions au sein de la boucle de auto mode.xlsx, Données et courbes - comportements statique et dynamique.xlsx, Fichier csv test résu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]
2022-12-20 nouveau mode calibration
    [Fichier csv test résultats - nuage de points.xlsx]
2023-01-02 réorganisation Janvier 2023
    [Comparaison des temps d'exécutions au sein de la boucle de auto mode.xlsx, Fichier csv test résultats - boîte à moustaches (1er test).xlsx, Fichier csv test ré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]
2023-01-02 test pour 1000
    [Fichier csv - nuage de points - 1er test pour 1000 - cas demi pour cent sur 3s.xlsx]
2023-01-04 affichage graph - calibration mode IHM
    [2023-01-04-10h16-Calibration_mode_Results.csv, Fichier csv - nuage de points - tests pour 1000.xlsx]
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2023-01-05 ajout record et feuille excel du test incrémentation 1 pour mille
    [2023-01-05-10h09-Calibration_mode_Results.csv, Fichier csv - nuage de points - tests pour 1000.xlsx]
2023-01-05 IHM et firmware version timers interrupt 250 pts par valeur consigne
    [2023-01-05-14h04-Calibration_mode_Results.csv, 2023-01-05-15h04-Calibration_mode_Results.csv, 2023-01-05-15h09-Calibration_mode_Results.csv, 2023-01-05-15h11-C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]
2023-01-06 rapport et autre
    [Fichier csv - Tests timer interrupt sur différentes counter periods.xlsx]
2023-01-09 données brutes
    [2023-01-09-14h11-Calibration_mode_Results.csv, 2023-01-09-14h32-Calibration_mode_Results.csv, 2023-01-09-15h01-Calibration_mode_Results.csv, 2023-01-09-16h24-C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]
2023-01-10 prospection dma
    [2023-01-10-11h23-Calibration_mode_Results.csv]
2023-01-16 possible solution pbm ihm readline
    [2023-01-16-11h41-Calibration_mode_Results.csv, 2023-01-16-11h44-Calibration_mode_Results.csv, 2023-01-16-11h52-Calibration_mode_Results.csv, 2023-01-16-11h55-C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]
2023-01-17 nouveau pbm synchro data
    [2023-01-17-10h11-Calibration_mode_Results.csv, 2023-01-17-10h18-Calibration_mode_Results.csv, 2023-01-17-10h32-Calibration_mode_Results.csv, 2023-01-17-10h35-C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]
2023-01-18 résolution pbm synchro + nouveaux graphes
    [2023-01-18-10h46-Calibration_mode_Results.csv, 2023-01-18-11h19-Calibration_mode_Results.csv, 2023-01-18-12h46-Calibration_mode_Results.csv, 2023-01-18-14h27-C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]
2023-01-20 dev IHM
    [2023-01-19-09h47-Calibration_mode_Results.csv]
2023-01-23 courbes et correction pbm
    [2023-01-23-09h49-Calibration_mode_Results.csv, 2023-01-23-09h58-Calibration_mode_Results.csv, 2023-01-23-10h00-Calibration_mode_Results.csv, 2023-01-23-10h13-C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]
2023-01-23 courbes 20V
    [2023-01-23-16h16-Calibration_mode_Results.csv, 2023-01-23-16h51-Calibration_mode_Results.csv, Fichier csv - tests 20V.xlsx, Fichier csv test résultats - courbe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]
2023-01-24 dev rapport
    [2023-01-24-16h18-Calibration_mode_Results.csv, Fichier csv test résultats - courbes statique et dynamique échelon 10%.xlsx]
2023-01-25 dev rapport + dev IHM et code C pour test trip - auto mode - données brutes
    [2023-01-25-10h18-Calibration_mode_Results.csv, 2023-01-25-10h29-Calibration_mode_Results.csv, 2023-01-25-10h31-Calibration_mode_Results.csv, 2023-01-25-10h44-C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]
2023-01-26 ajout erreurs pid
    [2023-01-26-10h45-Trip_mode_Results.csv, 2023-01-26-12h18-Trip_mode_Results.csv, 2023-01-26-12h34-Trip_mode_Results.csv, 2023-01-26-12h39-Trip_mode_Results.csv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]
2023-01-26 ajout courbe sans carter
    [2023-01-26-17h27-Calibration_mode_Results.csv, 2023-01-26-18h06-Calibration_mode_Results.csv, Fichier csv - 24V - sans carter.xlsx, Fichier csv - mode Trip 24V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]
2023-01-27 Add License.md
    [2023-01-26-10h45-Trip_mode_Results.csv, 2023-01-26-12h18-Trip_mode_Results.csv, 2023-01-26-12h34-Trip_mode_Results.csv, 2023-01-26-12h39-Trip_mode_Results.csv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]
2023-01-30 ajout courbe sans carter - séquence de vol
    [Fichier csv - mode Trip 24V - premiers tests.xlsx]
2023-01-30 tests coeff PID
    [2023-01-30-16h42-Trip_mode_Results.csv, 2023-01-30-16h50-Trip_mode_Results.csv, 2023-01-30-16h53-Trip_mode_Results.csv, 2023-01-30-16h54-Trip_mode_Results.csv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]
2023-01-31 dev schémas
    [2023-01-31-10h51-Trip_mode_Results.csv]
2023-02-01 dev show graph
    [2023-02-01-11h03-Trip_mode_Results.csv, 2023-02-01-11h07-Trip_mode_Results.csv, 2023-02-01-11h12-Calibration_mode_Results.csv, 2023-02-01-11h14-Trip_mode_Resul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]
2023-02-08 ajout graph calibration bras au repos
    [2023-02-08-14h46-Calibration_mode_Results.csv, 2023-02-08-15h43-Trip_mode_Results.csv, 2023-02-08-15h51-Calibration_mode_Results.csv, 2023-02-08-15h54-Calibrat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]
2023-02-10 tests ihm
    [2023-01-03-15h22-Calibration_mode_Results.csv, 2023-01-03-16h16-Calibration_mode_Results.csv, 2023-01-03-16h30-Calibration_mode_Results.csv, 2023-01-04-10h16-C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]
2023-02-13 tests pid + ajout courbes
    [2023-02-13-10h17-Calibration_mode_Results.csv, 2023-02-13-10h21-Calibration_mode_Results.csv, 2023-02-13-10h35-Trip_mode_Results.csv, 2023-02-13-11h38-Trip_mod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]
2023-02-14 modifs firmware
    [Comparaison des temps d'exécutions au sein de la boucle de auto mode.xlsx]
2023-02-15 changements glitch, asservissement interrupt, graphiques
    [2023-02-15-10h42-Trip_mode_Results.csv, Bras au repos pendant 30s.csv, Bras déplacé manuellement (sans gaz).csv, Calibration tous les 2‰ sur 5s.csv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]
2023-02-16 résoution pbm auto mode
    [2023-02-16-13h36-Trip_mode_Results.csv, 2023-02-16-15h39-Trip_mode_Results.csv]
2023-02-22 auto mode & trip mode même asservissement timer interrupt
    [2023-02-06-10h56-Trip_mode_Results.csv, 2023-02-06-10h59-Trip_mode_Results.csv, 2023-02-06-11h04-Calibration_mode_Results.csv, 2023-02-22-17h23-Trip_mode_Resul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]
2023-02-23 tests solidworks
    [Base_Assemblage.SLDPRT, Equerre_Assemblage.SLDPRT, Etude de cas 2.SLDPRT, Pièce fonctions - exemple.SLDPRT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]
2023-02-27 solidworks dans mdl
    [Base_Assemblage.SLDPRT, Equerre_Assemblage.SLDPRT, Etude de cas 2.SLDPRT, Pièce fonctions - exemple.SLDPRT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]
2023-02-27 ihm atterrissage d'urgence
    [2023-02-27-15h27-Trip_mode_Results.csv]
2023-03-02 tests threading
    [2023-03-02-15h27-Calibration_mode_Results.csv]
2023-03-22 nouveau carter stl
    [Test_carter_helice_rsV5.STL, nut_rs20.SLDPRT]
2023-03-22 rapport signé
    [2023-03-22-11h40-Trip_mode_Results.csv, 2023-03-22-11h57-Trip_mode_Results.csv]
2023-03-23 tests plotly
    [2023-01-03-15h22-Calibration_mode_Results.csv, 2023-01-03-16h16-Calibration_mode_Results.csv, 2023-01-03-16h30-Calibration_mode_Results.csv, 2023-01-04-10h16-C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]
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
